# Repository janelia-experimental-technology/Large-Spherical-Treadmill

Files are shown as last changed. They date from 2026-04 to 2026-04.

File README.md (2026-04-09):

### Large Spherical Treadmill

Abstract

Recent advances in the use of the awake, head-fixed preparation for small rodents (e.g., rats and mice) have led to an array of new interactive tools for studying brain and behavior. Here we present a method for creating large, lightweight spherical treadmills of arbitrary size. To accommodate different treadmill sizes, we provide a sparse, point-based floatation mechanism that is highly scalable.

For mice (8-12 wk, 20-30 g), we present a 16” (40.64 cm, approx. 65-70 g) diameter spherical treadmill. For young-adult rats (3-8 wk, 60-150 g), we present a 24” (60.96 cm, approx. 225-275 g) diameter system.

Features \& Benefits:

&#x20;   A larger spherical diameter creates a flatter treadmill surface area that allows for a more comfortable animal and positively promotes the expression of natural behaviors (sleeping, resting, grooming, and goal-directed walking and running).

&#x20;   The point-based floatation system reduces oscillations in air-flow around the treadmill and provides excellent stability under different behavioral and recording conditions.

&#x20;   The point-based floatation and minimal frame design accommodate well for slight irregularities in, and differences between, the size of individual spherical treadmills

&#x20;   The point-based floatation system reduces air-flow and system volume

&#x20;   The minimal frame design allows for increased access to the lower half of the treadmill surface for motion-tracking and other potential manipulations

Opportunity: Free to make for Non-Profit Research by downloading the design here. See included hardware license.

Rights and designs available for Commercial License. Janelia makes no endorsements or guarantees of licensee products.

For inquiries, please contact innovation@janelia.hhmi.org and reference this repository.

To cite the designs, please use DOI: https://doi.org/10.25378/janelia.31974762

Supercedes Flintbox ID 2012-019

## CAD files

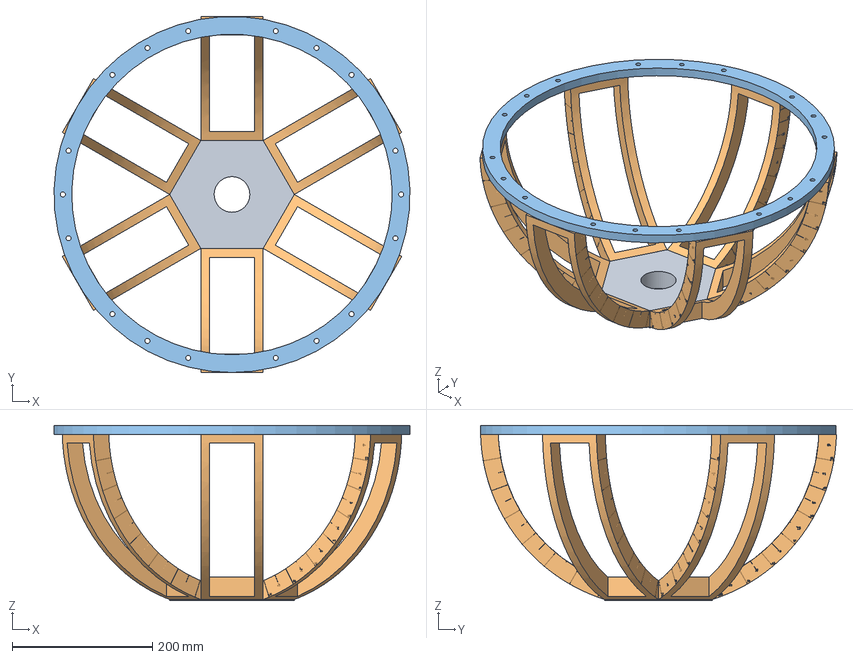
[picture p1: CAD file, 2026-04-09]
Part Drawings and Models/JF-AT-TM0006 16 inch ball treadmill assembly Rev -.stp
507.8 x 507.9 x 250.0 mm
16 inch ball treadmill frame base v2
16 inch ball treadmill frame v2 x 6
16 inch ball treadmill top ring v2

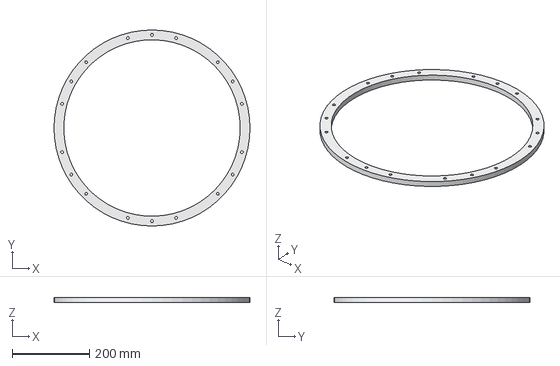
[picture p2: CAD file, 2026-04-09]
Part Drawings and Models/JF-AT-TM0008 16 inch ball treadmill top ring v2 Rev -.stp
508.0 x 508.0 x 12.7 mm

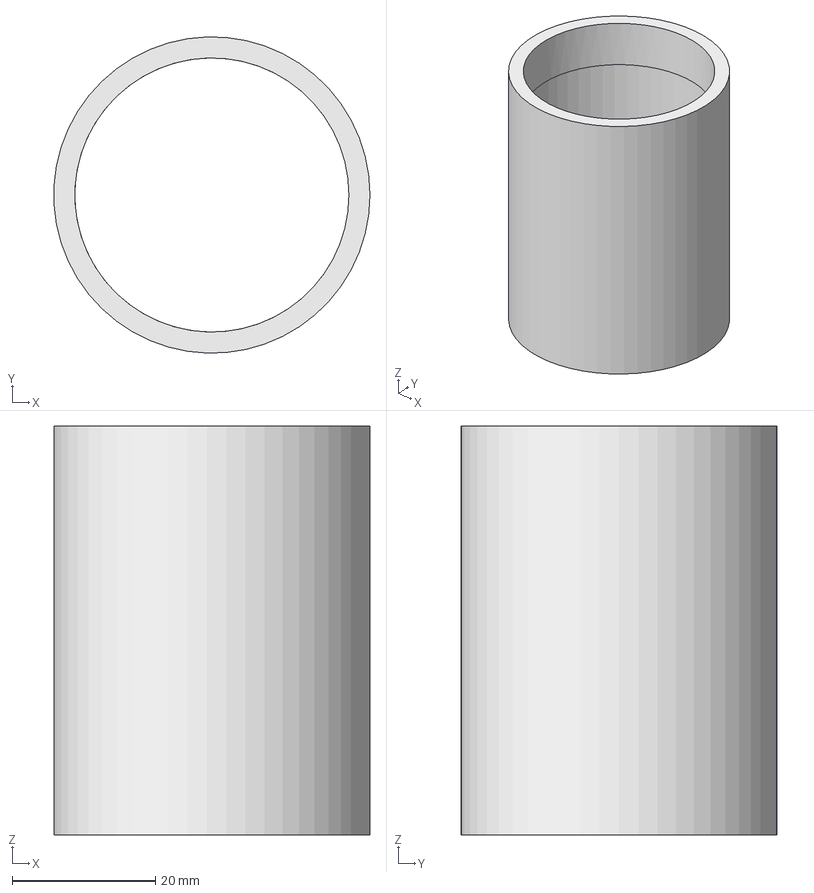
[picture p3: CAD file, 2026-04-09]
Part Drawings and Models/JF-AT-JC0005 BallHolderTubeAirBall Rev C.stp
44.2 x 44.2 x 57.1 mm

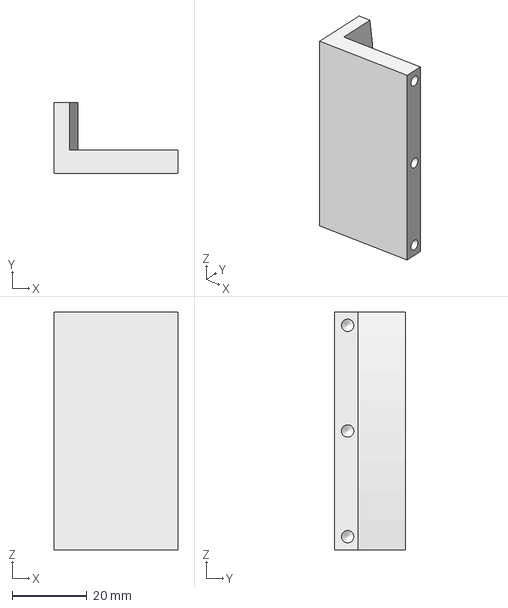
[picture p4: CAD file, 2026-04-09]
Part Drawings and Models/JF-AT-JC0016 CanClamper16 Rev A.stp
33.0 x 19.1 x 63.5 mm

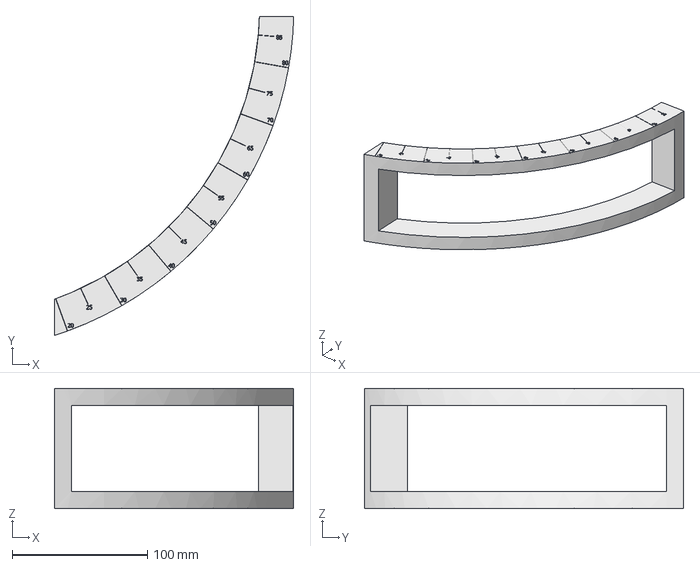
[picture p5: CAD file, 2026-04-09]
Part Drawings and Models/JF-AT-TM0007 16 inch ball treadmill frame v2 Rev -.stp
176.9 x 235.7 x 88.9 mm

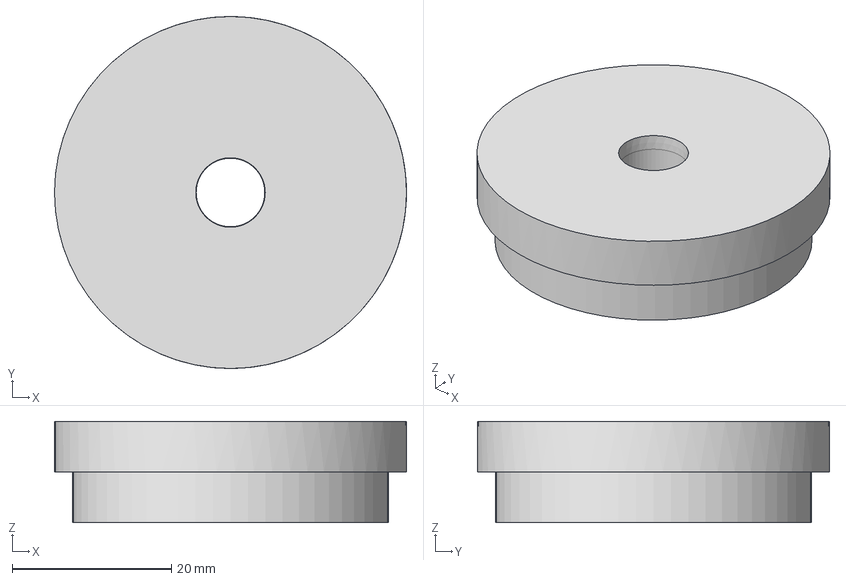
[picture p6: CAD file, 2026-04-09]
Part Drawings and Models/JF-AT-TC0007 BottomCapAirBall Rev B.stp
44.2 x 44.2 x 12.7 mm

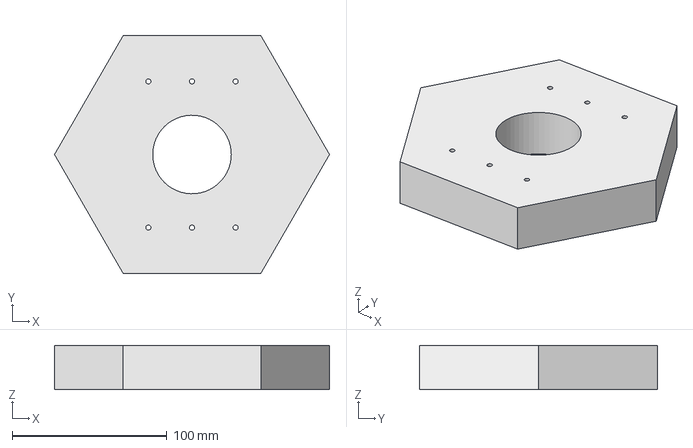
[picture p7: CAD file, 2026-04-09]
Part Drawings and Models/JF-AT-TM0009 16 inch ball treadmill frame base v2 Rev A.stp
177.8 x 154.0 x 28.4 mm

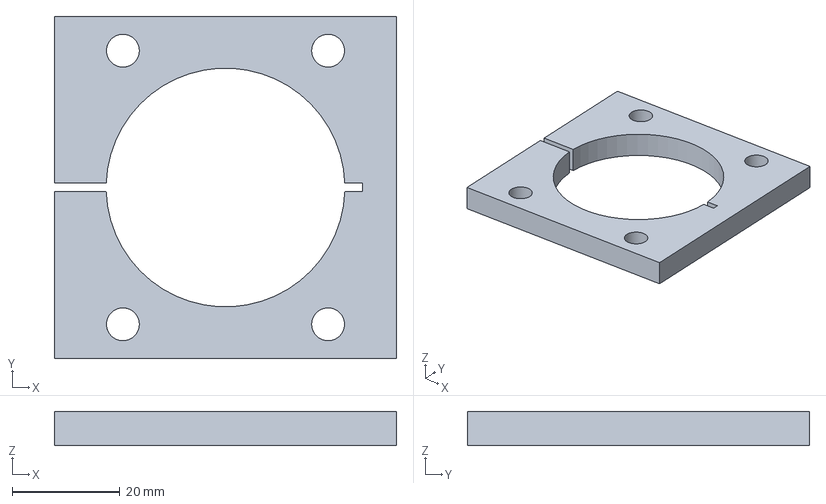
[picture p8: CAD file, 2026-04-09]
Part Drawings and Models/JF-AT-JC0015 CanClamp Rev -.stp
63.5 x 63.5 x 6.35 mm

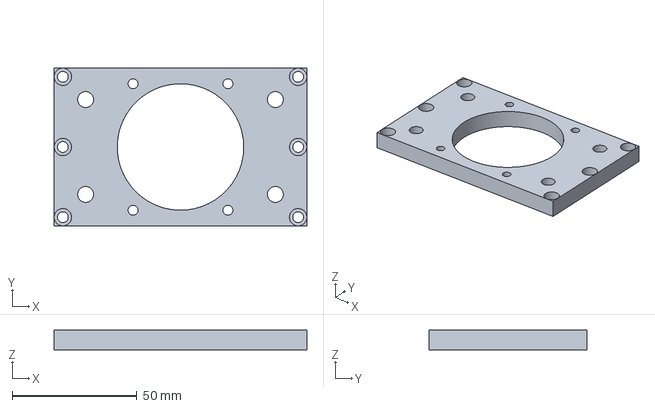
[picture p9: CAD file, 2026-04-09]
Part Drawings and Models/JF-AT-JC0014 ClamperPlate Rev -.stp
101.6 x 63.5 x 7.94 mm

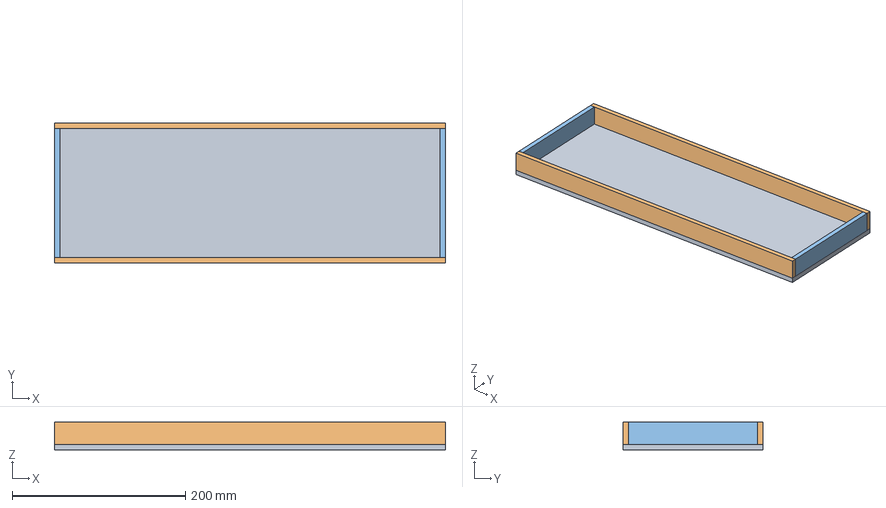
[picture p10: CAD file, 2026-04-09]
Part Drawings and Models/J005217 MBS TROUGH ASSY Rev -.stp
450.9 x 161.9 x 31.8 mm
MBS TROUGH BASE
MBS TROUGH SIDE x 2
MBS TROUGH END x 2

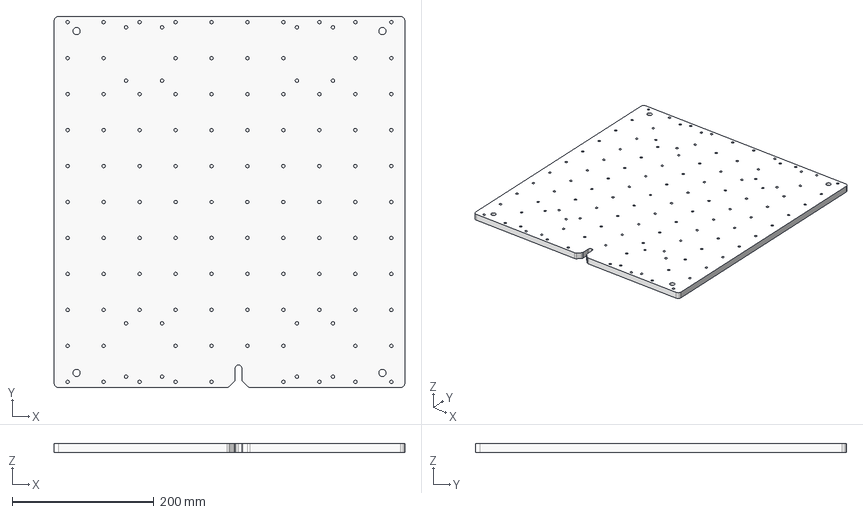
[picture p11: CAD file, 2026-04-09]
Part Drawings and Models/J003049 MBS Ball Base Plate Rev A.stp
495.3 x 523.8 x 12.7 mm

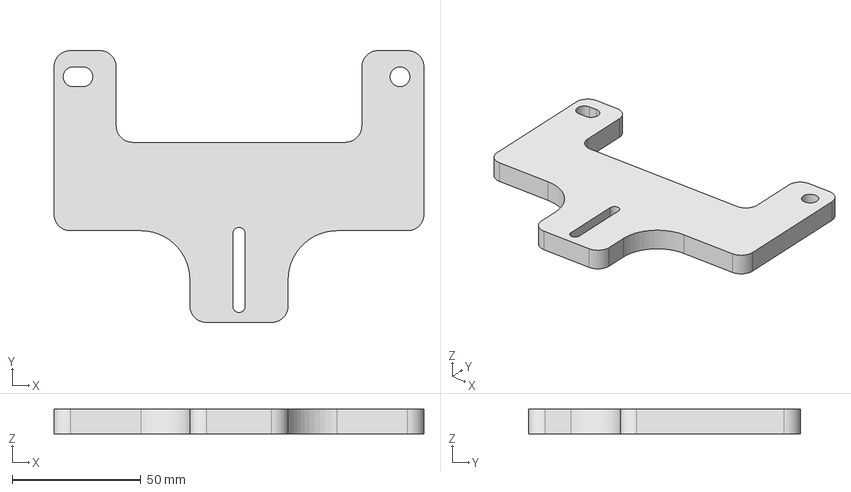
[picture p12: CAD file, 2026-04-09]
Part Drawings and Models/J005643 MBS Camera Bracket Rev -.stp
143.5 x 105.4 x 9.52 mm

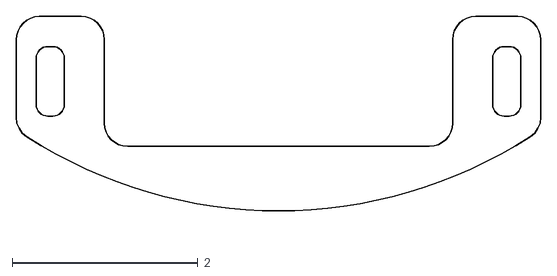
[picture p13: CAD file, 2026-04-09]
Part Drawings and Models/J005684 MBS SIDE GUIDE CONVEX Rev -.dxf
5.65 x 2.36

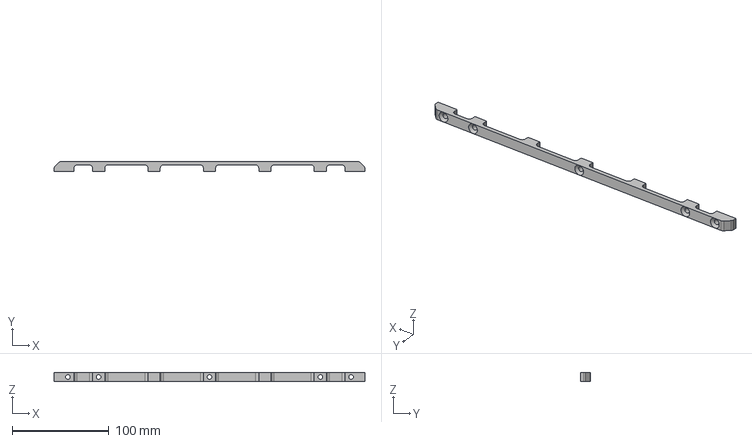
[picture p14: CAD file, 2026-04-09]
Part Drawings and Models/J005229 MBS TROUGH RAIL REV -.stp
320.7 x 10.8 x 9.52 mm

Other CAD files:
Part Drawings and Models/J005683 Ribbon Cable Connector.stp
Part Drawings and Models/J005679 Camera Front body.stp
Part Drawings and Models/J005209 MBS REG BASE PLATE REV -.stp
Part Drawings and Models/J005681 Camera Back Plate.stp
Pack and Go-Inventor Models/03-618.ipt
Pack and Go-Inventor Models/16 inch ball treadmill assembly.iam
Pack and Go-Inventor Models/16 inch ball treadmill frame base v2.ipt
Pack and Go-Inventor Models/16 inch ball treadmill frame v2.ipt
Pack and Go-Inventor Models/16 inch ball treadmill top ring v2.ipt
Pack and Go-Inventor Models/321527B00000G.ipt
Pack and Go-Inventor Models/50745K150.ipt
Pack and Go-Inventor Models/50785K213.ipt
Pack and Go-Inventor Models/50785K410.ipt
Pack and Go-Inventor Models/5779K109.ipt
Pack and Go-Inventor Models/5779K143.ipt
Pack and Go-Inventor Models/6516T13.ipt
Pack and Go-Inventor Models/90107A010.ipt
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

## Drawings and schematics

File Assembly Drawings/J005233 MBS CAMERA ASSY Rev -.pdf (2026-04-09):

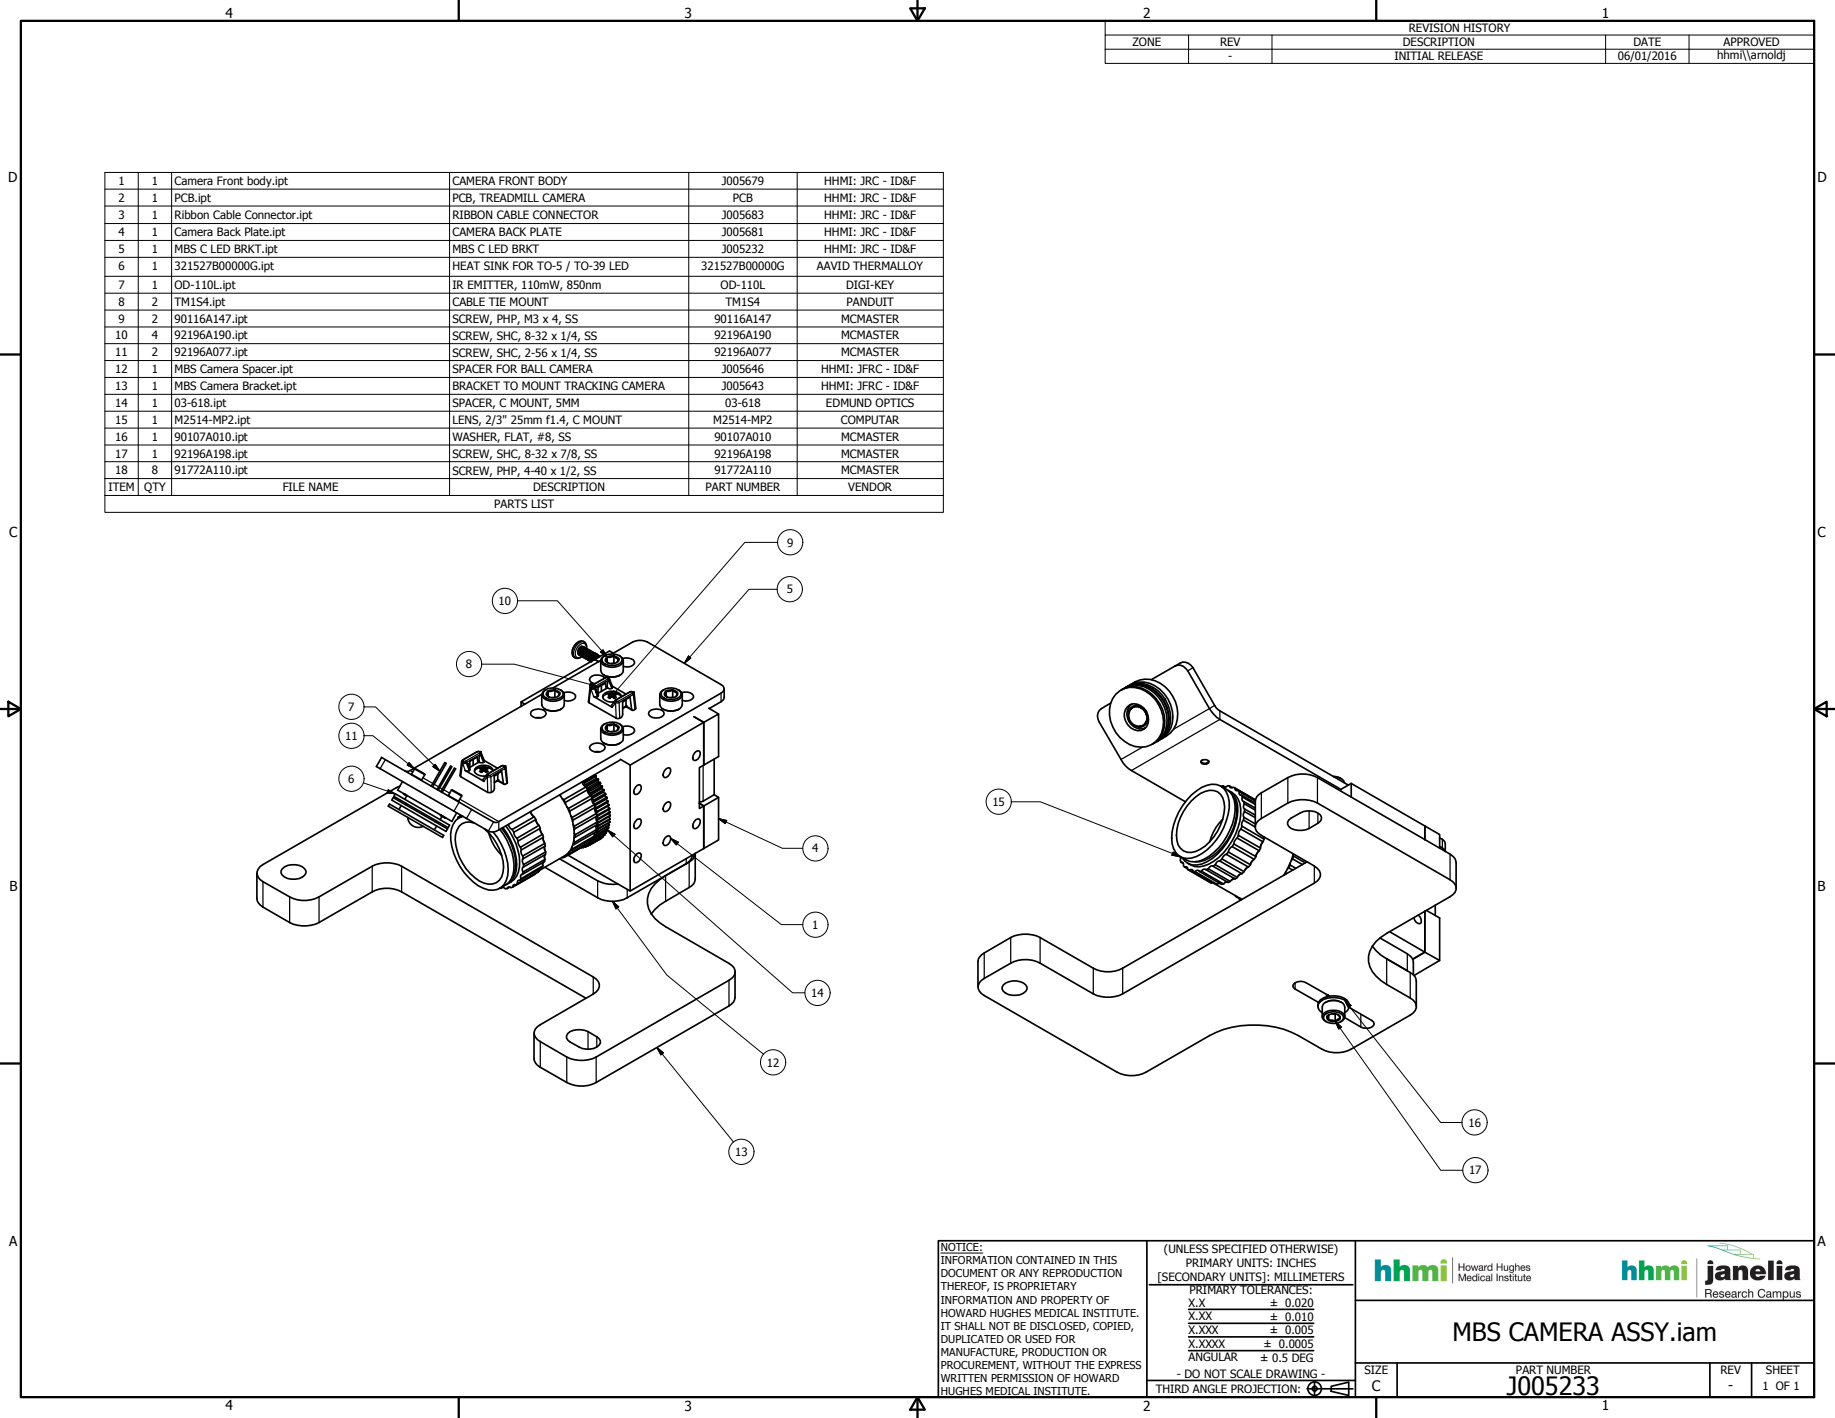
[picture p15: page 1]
Camera Front body.ipt; CAMERA FRONT BODY; HHMI: JRC - ID&F; PCB.ipt; PCB, TREADMILL CAMERA; PCB; Ribbon Cable Connector.ipt; RIBBON CABLE CONNECTOR; Camera Back Plate.ipt; CAMERA BACK PLATE; MBS C LED BRKT.ipt; MBS C LED BRKT; 321527B00000G.ipt; HEAT SINK FOR TO-5 / TO-39 LED; AAVID THERMALLOY; OD-110L.ipt; IR EMITTER, 110mW, 850nm; DIGI-KEY; TM1S4.ipt; CABLE TIE MOUNT; PANDUIT; 90116A147.ipt; SCREW, PHP, M3 x 4, SS; MCMASTER; 92196A190.ipt; SCREW, SHC, 8-32 x 1/4, SS; 92196A077.ipt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

NOTICE:
INFORMATION CONTAINED IN THIS
DOCUMENT OR ANY REPRODUCTION
THEREOF, IS PROPRIETARY
INFORMATION AND PROPERTY OF
HOWARD HUGHES MEDICAL INSTITUTE.
IT SHALL NOT BE DISCLOSED, COPIED,
DUPLICATED OR USED FOR
MANUFACTURE, PRODUCTION OR
PROCUREMENT, WITHOUT THE EXPRESS
WRITTEN PERMISSION OF HOWARD
HUGHES MEDICAL INSTITUTE.

(UNLESS SPECIFIED OTHERWISE)
PRIMARY UNITS: INCHES
[SECONDARY UNITS]: MILLIMETERS
PRIMARY TOLERANCES:
X.XXX
X.XXXX
ANGULAR
- DO NOT SCALE DRAWING -

MBS CAMERA ASSY.iam

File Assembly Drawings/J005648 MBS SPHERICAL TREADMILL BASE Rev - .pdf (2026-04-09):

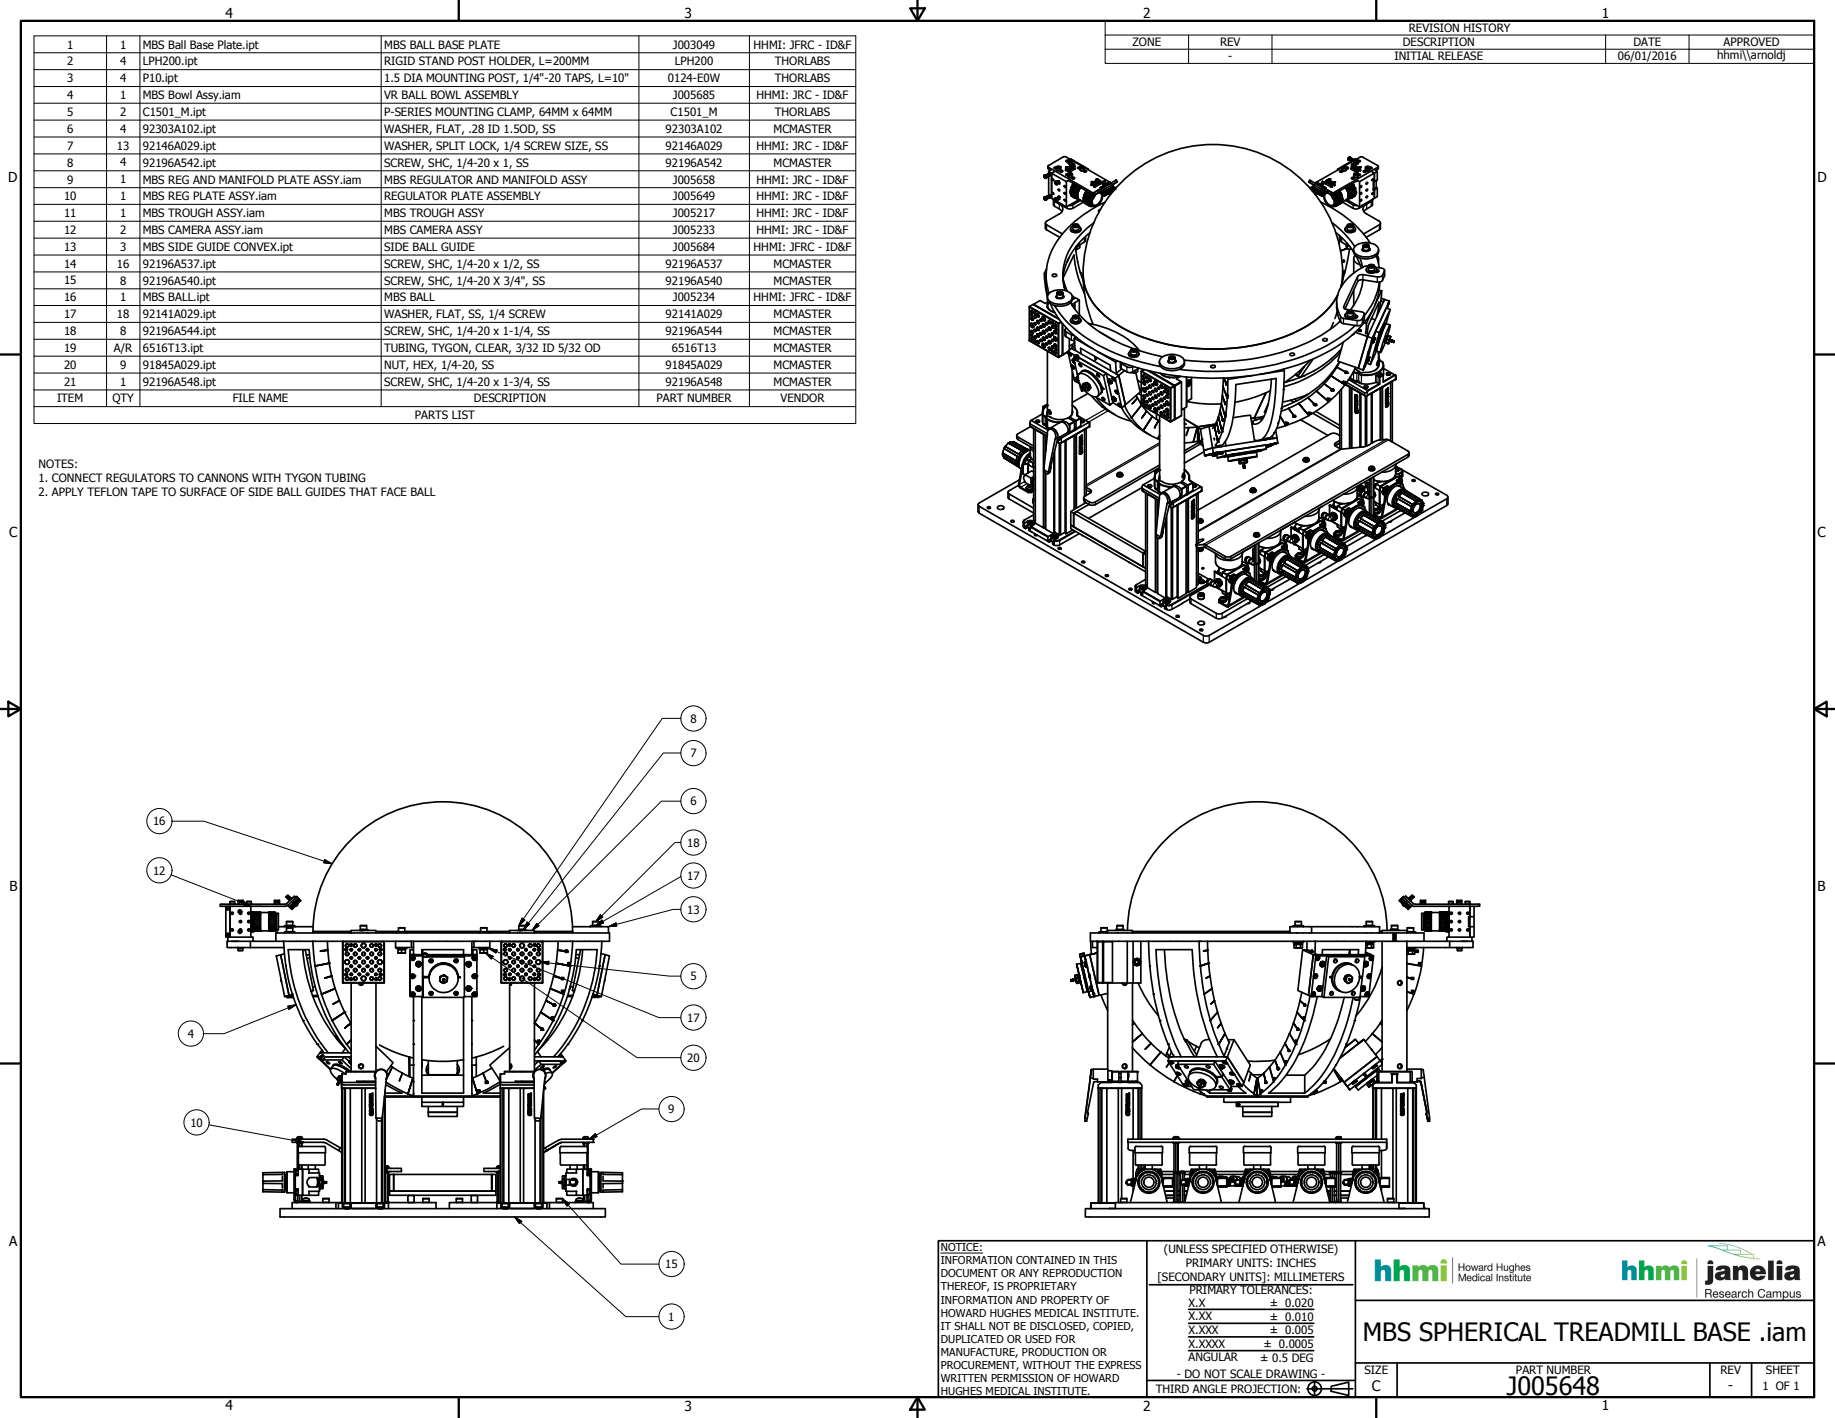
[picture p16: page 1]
MBS Ball Base Plate.ipt; MBS BALL BASE PLATE; HHMI: JFRC - ID&F; LPH200.ipt; RIGID STAND POST HOLDER, L=200MM; LPH200; THORLABS; P10.ipt; 1.5 DIA MOUNTING POST, 1/4"-20 TAPS, L=10"; MBS Bowl Assy.iam; VR BALL BOWL ASSEMBLY; HHMI: JRC - ID&F; C1501_M.ipt; P-SERIES MOUNTING CLAMP, 64MM x 64MM; 92303A102.ipt; WASHER, FLAT, .28 ID 1.5OD, SS; MCMASTER; 13 92146A029.ipt; WASHER, SPLIT LOCK, 1/4 SCREW SIZE, SS; 92196A542.ipt; SCREW, SHC, 1/4-20 x 1, SS; MBS REG AND MANIFOLD PLATE ASSY.iam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

NOTES:
1. CONNECT REGULATORS TO CANNONS WITH TYGON TUBING
2. APPLY TEFLON TAPE TO SURFACE OF SIDE BALL GUIDES THAT FACE BALL

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

MBS SPHERICAL TREADMILL BASE .iam

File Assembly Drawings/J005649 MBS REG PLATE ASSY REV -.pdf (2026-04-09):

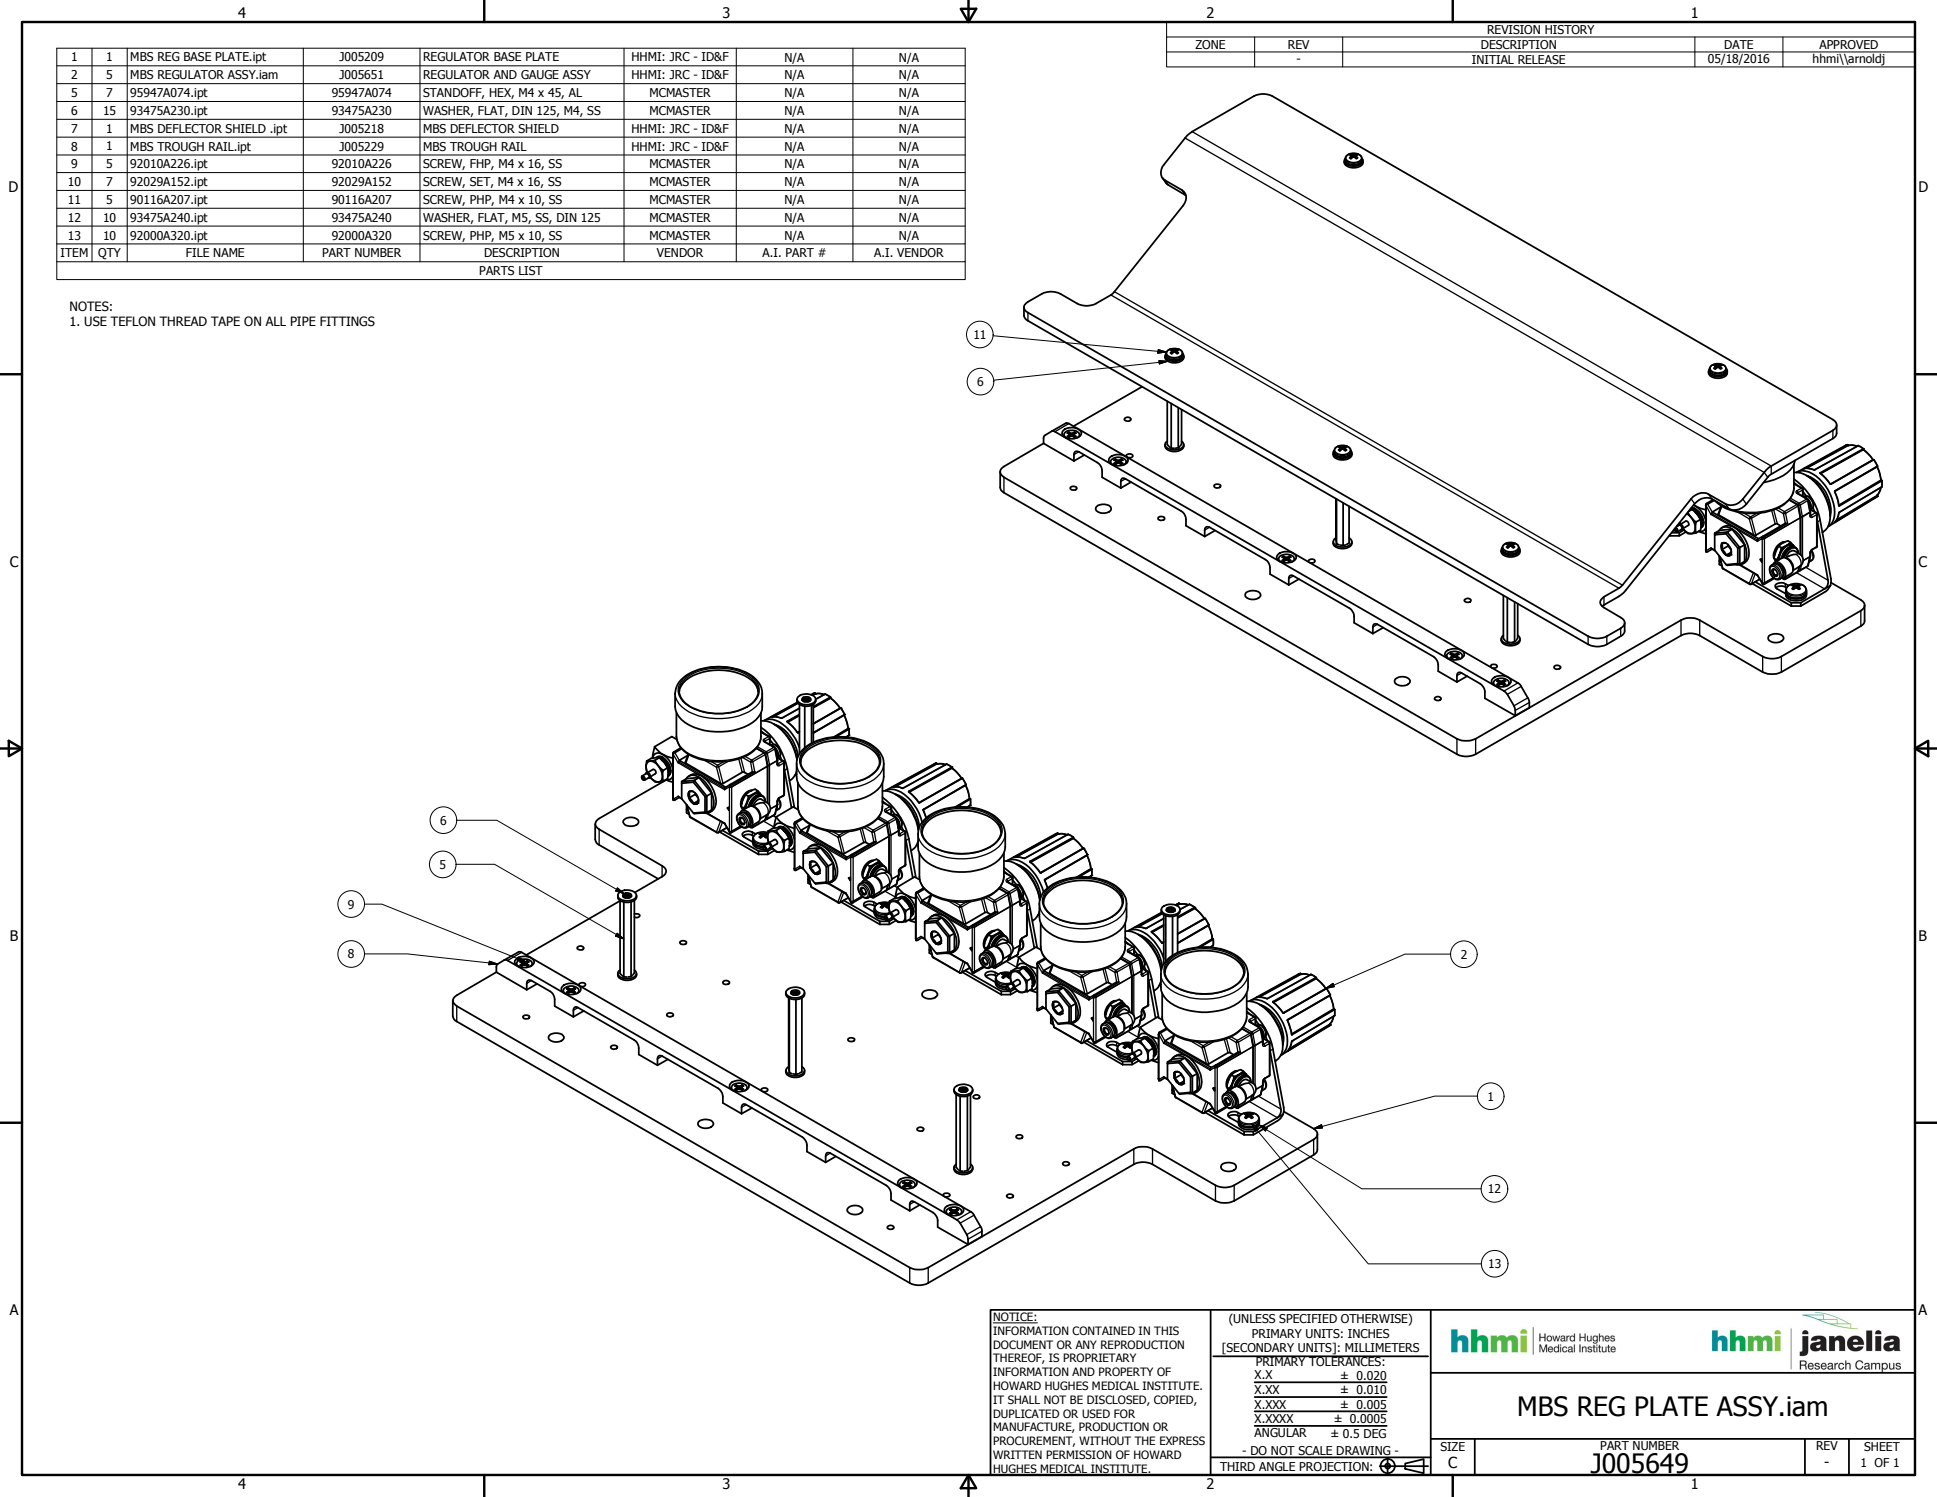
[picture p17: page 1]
92000A320.ipt; SCREW, PHP, M5 x 10, SS; MCMASTER; PARTS LIST; ITEM; QTY; FILE NAME; PART NUMBER; DESCRIPTION; VENDOR; A.I. PART #; A.I. VENDOR; SIZE; REV; SHEET; 1 OF 1 THIRD ANGLE PROJECTION:; ± 0.020 ± 0.010 ± 0.005 ± 0.0005 ± 0.5 DEG; REVISION HISTORY; ZONE; DATE; APPROVED; INITIAL RELEASE; hhmi\\arnoldj

1 | 1 | MBS REG BASE PLATE.ipt | J005209 | REGULATOR BASE PLATE | HHMI: JRC - ID&F | N/A | N/A
2 | 5 | MBS REGULATOR ASSY.iam | J005651 | REGULATOR AND GAUGE ASSY | HHMI: JRC - ID&F | N/A | N/A
5 | 7 | 95947A074.ipt | 95947A074 | STANDOFF, HEX, M4 x 45, AL | MCMASTER | N/A | N/A
6 | 15 | 93475A230.ipt | 93475A230 | WASHER, FLAT, DIN 125, M4, SS | MCMASTER | N/A | N/A
7 | 1 | MBS DEFLECTOR SHIELD .ipt | J005218 | MBS DEFLECTOR SHIELD | HHMI: JRC - ID&F | N/A | N/A
8 | 1 | MBS TROUGH RAIL.ipt | J005229 | MBS TROUGH RAIL | HHMI: JRC - ID&F | N/A | N/A
9 | 5 | 92010A226.ipt | 92010A226 | SCREW, FHP, M4 x 16, SS | MCMASTER | N/A | N/A
10 | 7 | 92029A152.ipt | 92029A152 | SCREW, SET, M4 x 16, SS | MCMASTER | N/A | N/A
11 | 5 | 90116A207.ipt | 90116A207 | SCREW, PHP, M4 x 10, SS | MCMASTER | N/A | N/A
12 | 10 | 93475A240.ipt | 93475A240 | WASHER, FLAT, M5, SS, DIN 125 | MCMASTER | N/A | N/A

NOTES:
1. USE TEFLON THREAD TAPE ON ALL PIPE FITTINGS

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

MBS REG PLATE ASSY.iam

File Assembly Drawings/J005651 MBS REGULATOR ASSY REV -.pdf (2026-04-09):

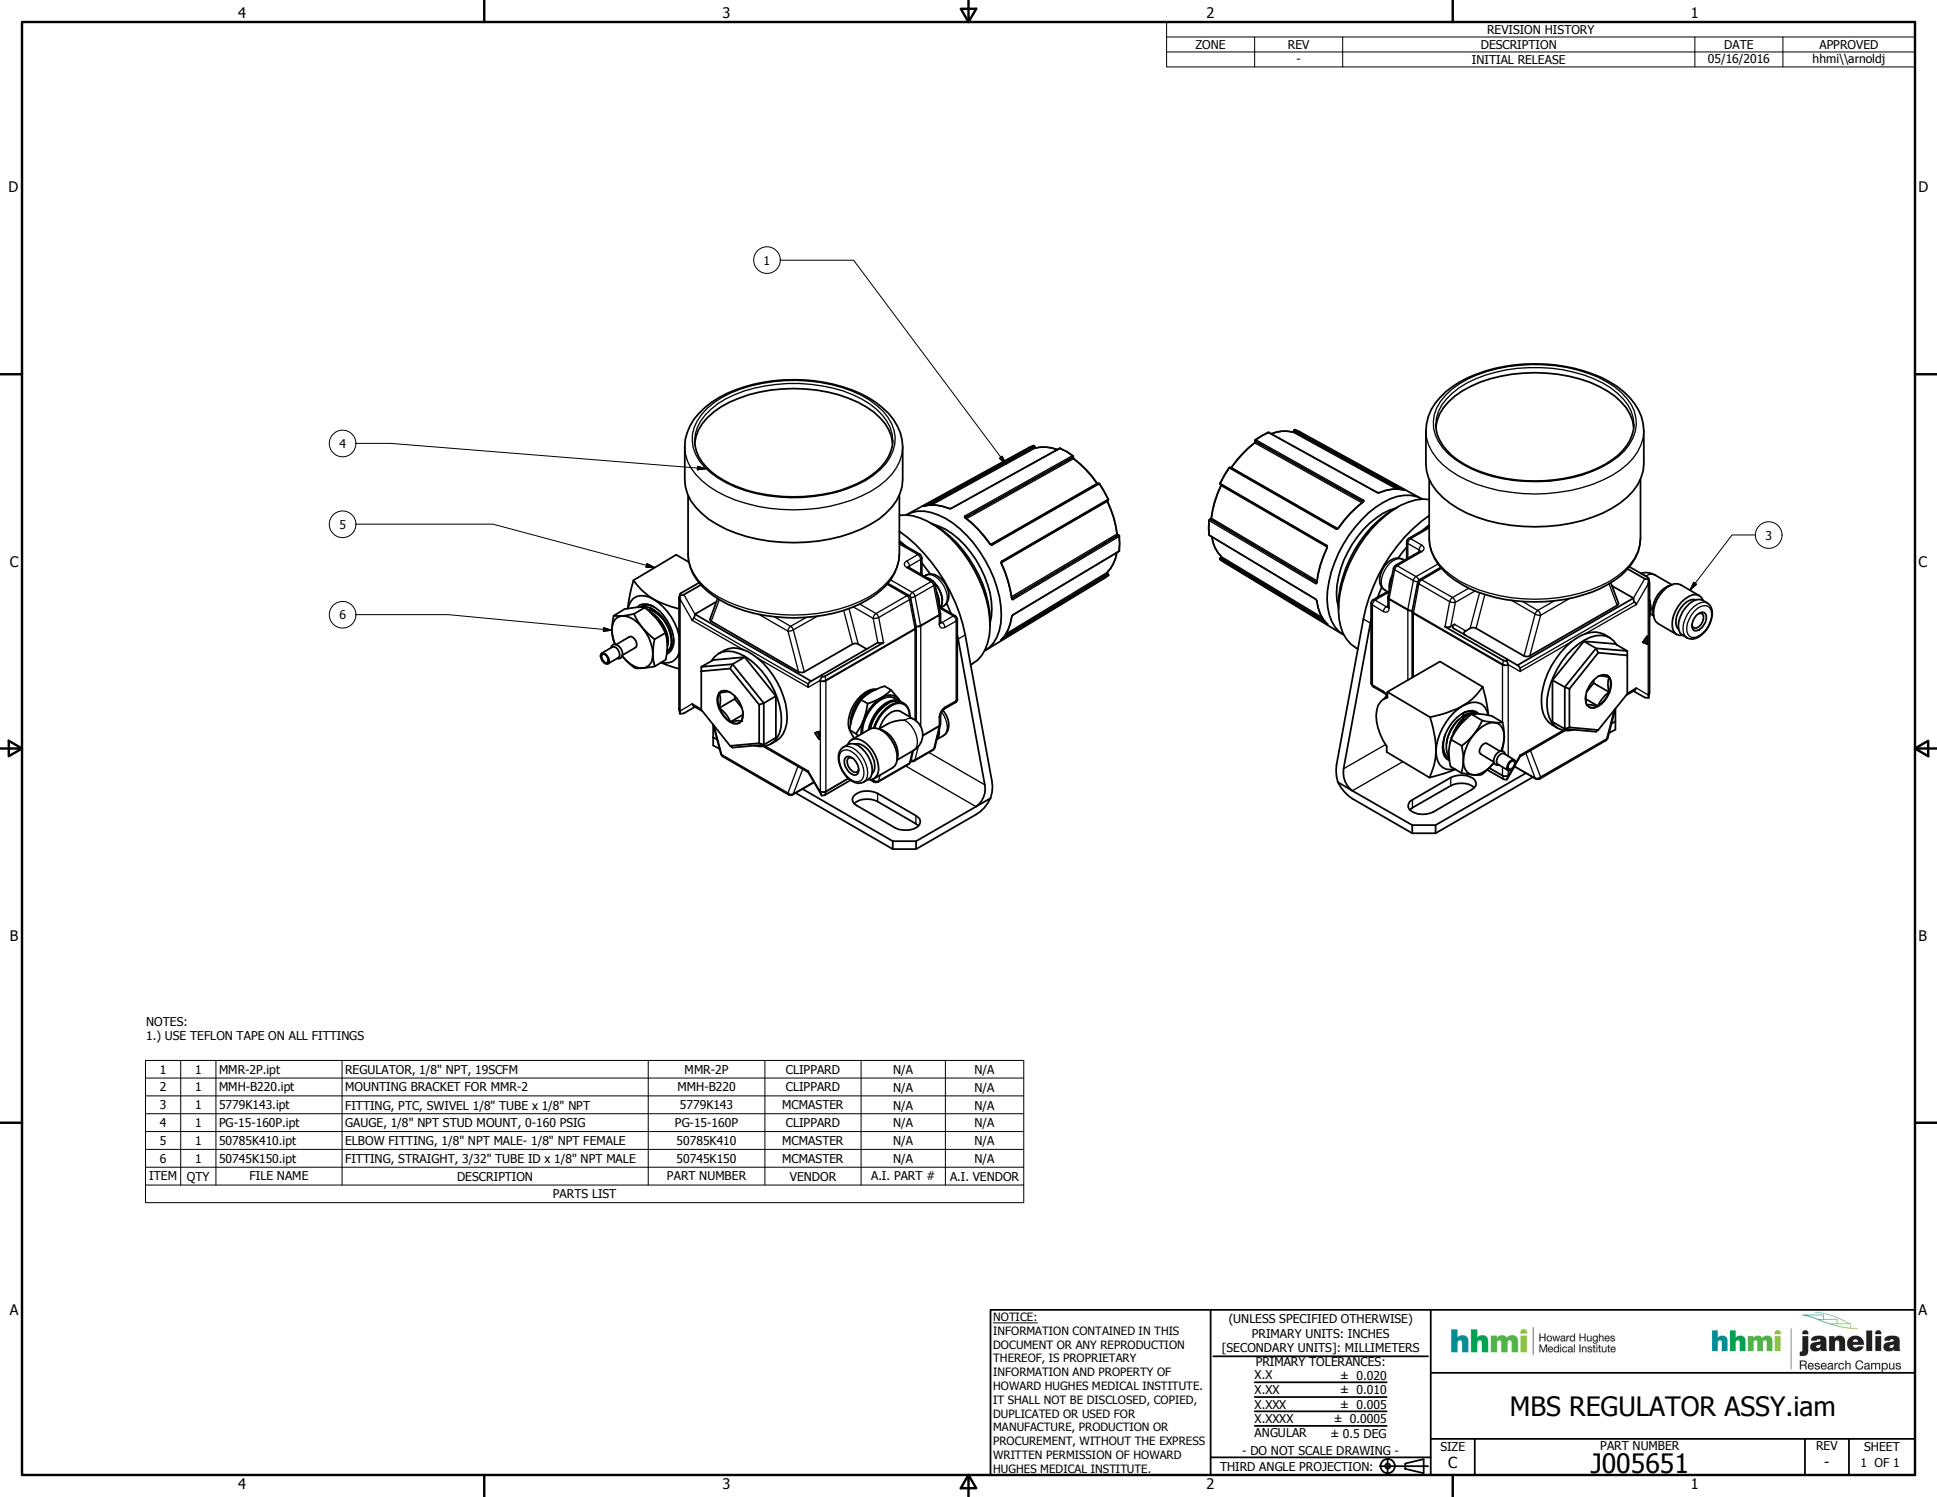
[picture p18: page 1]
MMR-2P.ipt; REGULATOR, 1/8" NPT, 19SCFM; MMR-2P; CLIPPARD; MMH-B220.ipt; MOUNTING BRACKET FOR MMR-2; MMH-B220; 5779K143.ipt; FITTING, PTC, SWIVEL 1/8" TUBE x 1/8" NPT; MCMASTER; PG-15-160P.ipt; GAUGE, 1/8" NPT STUD MOUNT, 0-160 PSIG; 50785K410.ipt; ELBOW FITTING, 1/8" NPT MALE- 1/8" NPT FEMALE; 50745K150.ipt; FITTING, STRAIGHT, 3/32" TUBE ID x 1/8" NPT MALE; PARTS LIST; ITEM; QTY; FILE NAME; DESCRIPTION; PART NUMBER; VENDOR; A.I. PART #; A.I. VENDOR; SIZE; REV; SHEET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

NOTES:
1.) USE TEFLON TAPE ON ALL FITTINGS

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

MBS REGULATOR ASSY.iam

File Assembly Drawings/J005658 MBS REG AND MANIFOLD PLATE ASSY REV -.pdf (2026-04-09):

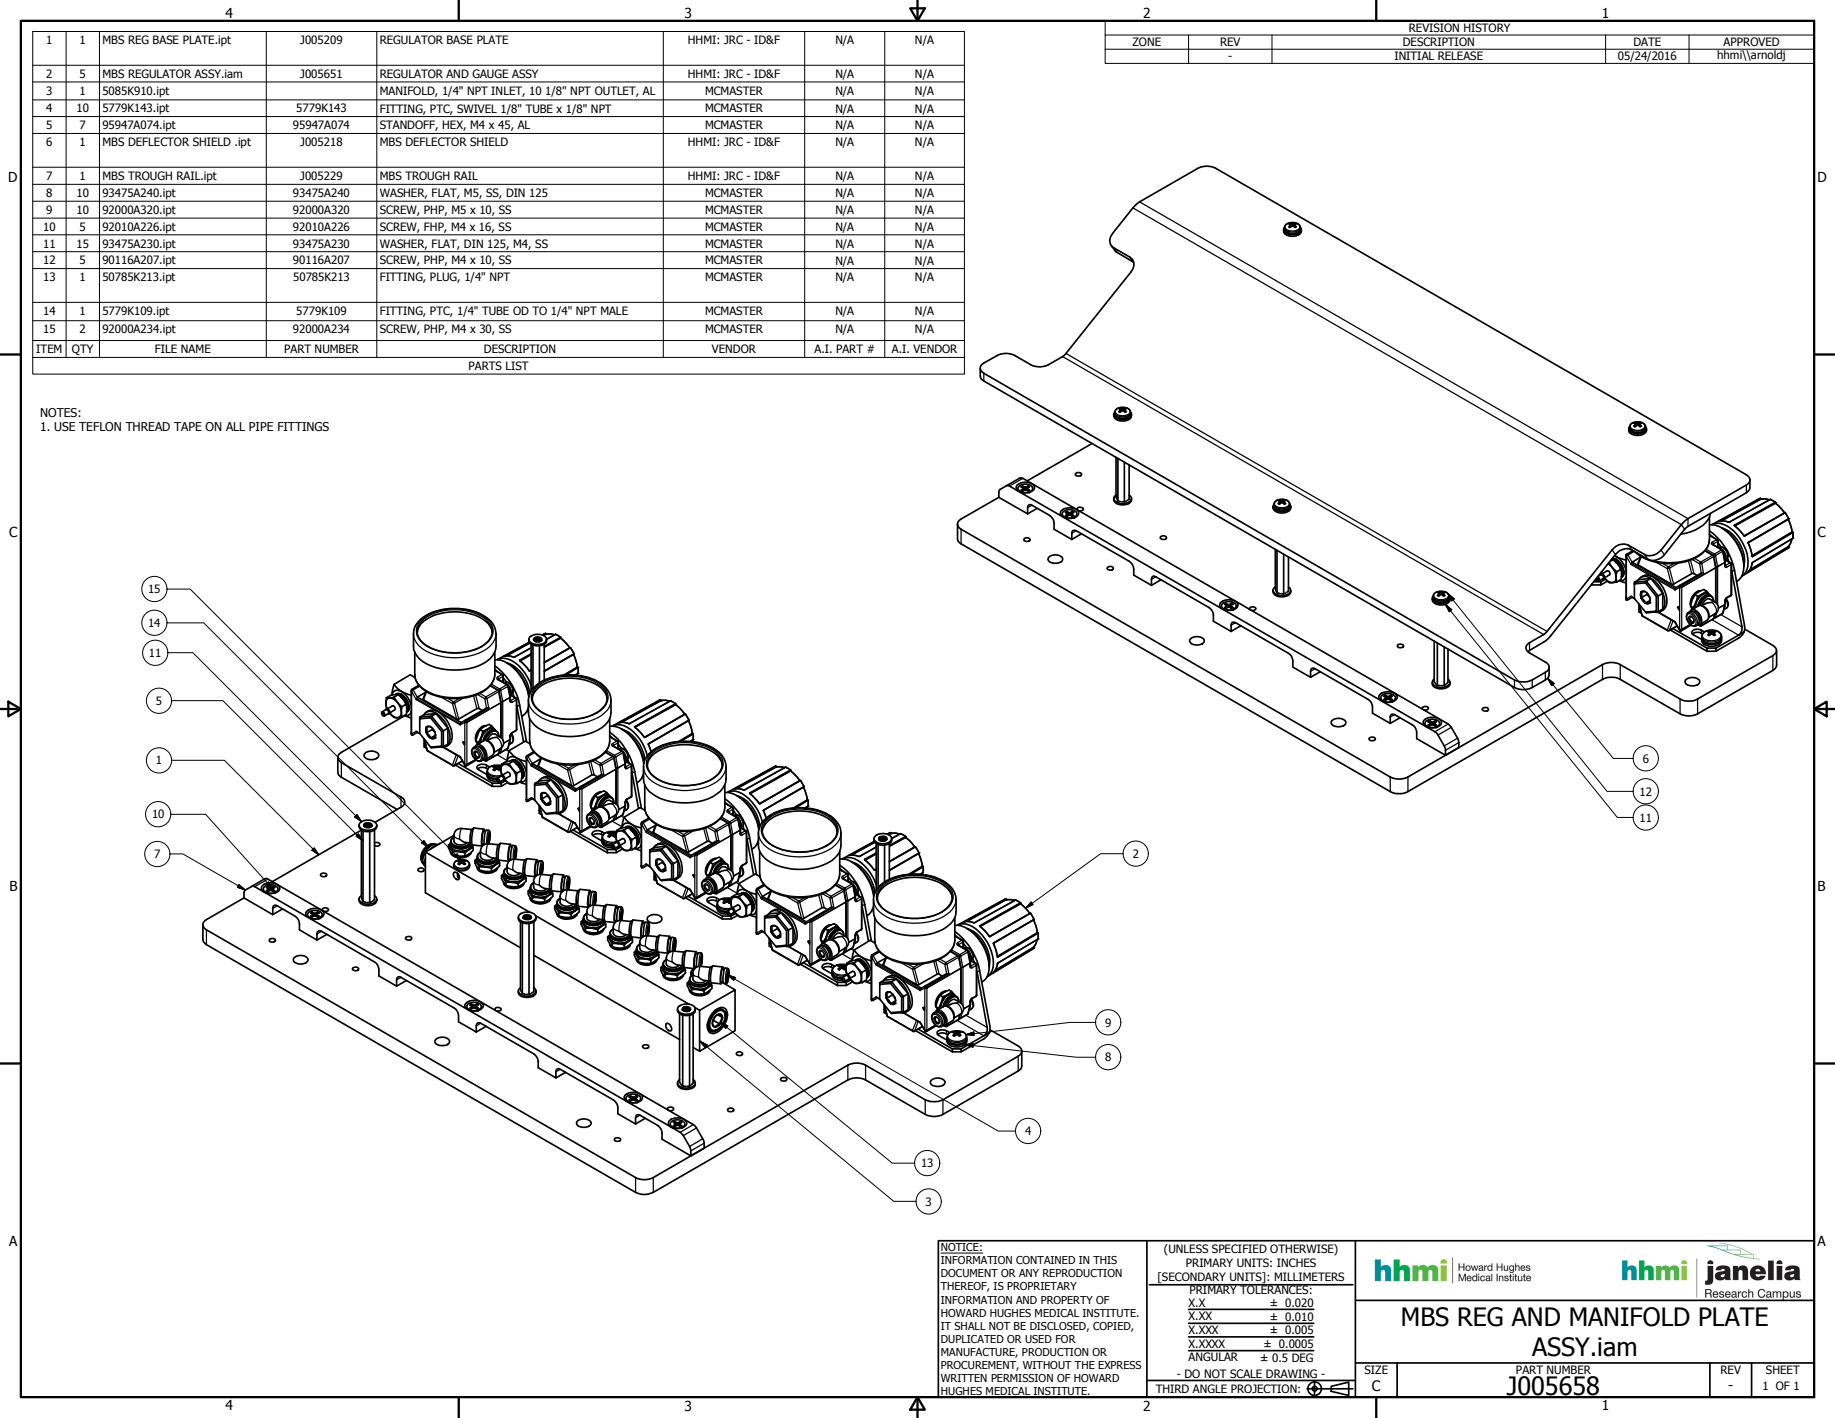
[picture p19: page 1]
MBS REG BASE PLATE.ipt; REGULATOR BASE PLATE; HHMI: JRC - ID&F; 92000A234.ipt; SCREW, PHP, M4 x 30, SS; MCMASTER; PARTS LIST; ITEM; QTY; FILE NAME; PART NUMBER; DESCRIPTION; VENDOR; A.I. PART #; A.I. VENDOR; SIZE; REV; SHEET; 1 OF 1 THIRD ANGLE PROJECTION:; ± 0.020 ± 0.010 ± 0.005 ± 0.0005 ± 0.5 DEG; ASSY.iam; REVISION HISTORY; ZONE; DATE; APPROVED; INITIAL RELEASE; hhmi\\arnoldj

2 | 5 | MBS REGULATOR ASSY.iam | J005651 | REGULATOR AND GAUGE ASSY | HHMI: JRC - ID&F | N/A | N/A
3 | 1 | 5085K910.ipt | | MANIFOLD, 1/4" NPT INLET, 10 1/8" NPT OUTLET, AL | MCMASTER | N/A | N/A
4 | 10 | 5779K143.ipt | 5779K143 | FITTING, PTC, SWIVEL 1/8" TUBE x 1/8" NPT | MCMASTER | N/A | N/A
5 | 7 | 95947A074.ipt | 95947A074 | STANDOFF, HEX, M4 x 45, AL | MCMASTER | N/A | N/A
6 | 1 | MBS DEFLECTOR SHIELD .ipt | J005218 | MBS DEFLECTOR SHIELD | HHMI: JRC - ID&F | N/A | N/A

7 | 1 | MBS TROUGH RAIL.ipt | J005229 | MBS TROUGH RAIL | HHMI: JRC - ID&F | N/A | N/A
8 | 10 | 93475A240.ipt | 93475A240 | WASHER, FLAT, M5, SS, DIN 125 | MCMASTER | N/A | N/A
9 | 10 | 92000A320.ipt | 92000A320 | SCREW, PHP, M5 x 10, SS | MCMASTER | N/A | N/A
10 | 5 | 92010A226.ipt | 92010A226 | SCREW, FHP, M4 x 16, SS | MCMASTER | N/A | N/A
11 | 15 | 93475A230.ipt | 93475A230 | WASHER, FLAT, DIN 125, M4, SS | MCMASTER | N/A | N/A
12 | 5 | 90116A207.ipt | 90116A207 | SCREW, PHP, M4 x 10, SS | MCMASTER | N/A | N/A
13 | 1 | 50785K213.ipt | 50785K213 | FITTING, PLUG, 1/4" NPT | MCMASTER | N/A | N/A

14 | 1 | 5779K109.ipt | 5779K109 | FITTING, PTC, 1/4" TUBE OD TO 1/4" NPT MALE | MCMASTER | N/A | N/A

NOTES:
1. USE TEFLON THREAD TAPE ON ALL PIPE FITTINGS

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

MBS REG AND MANIFOLD PLATE

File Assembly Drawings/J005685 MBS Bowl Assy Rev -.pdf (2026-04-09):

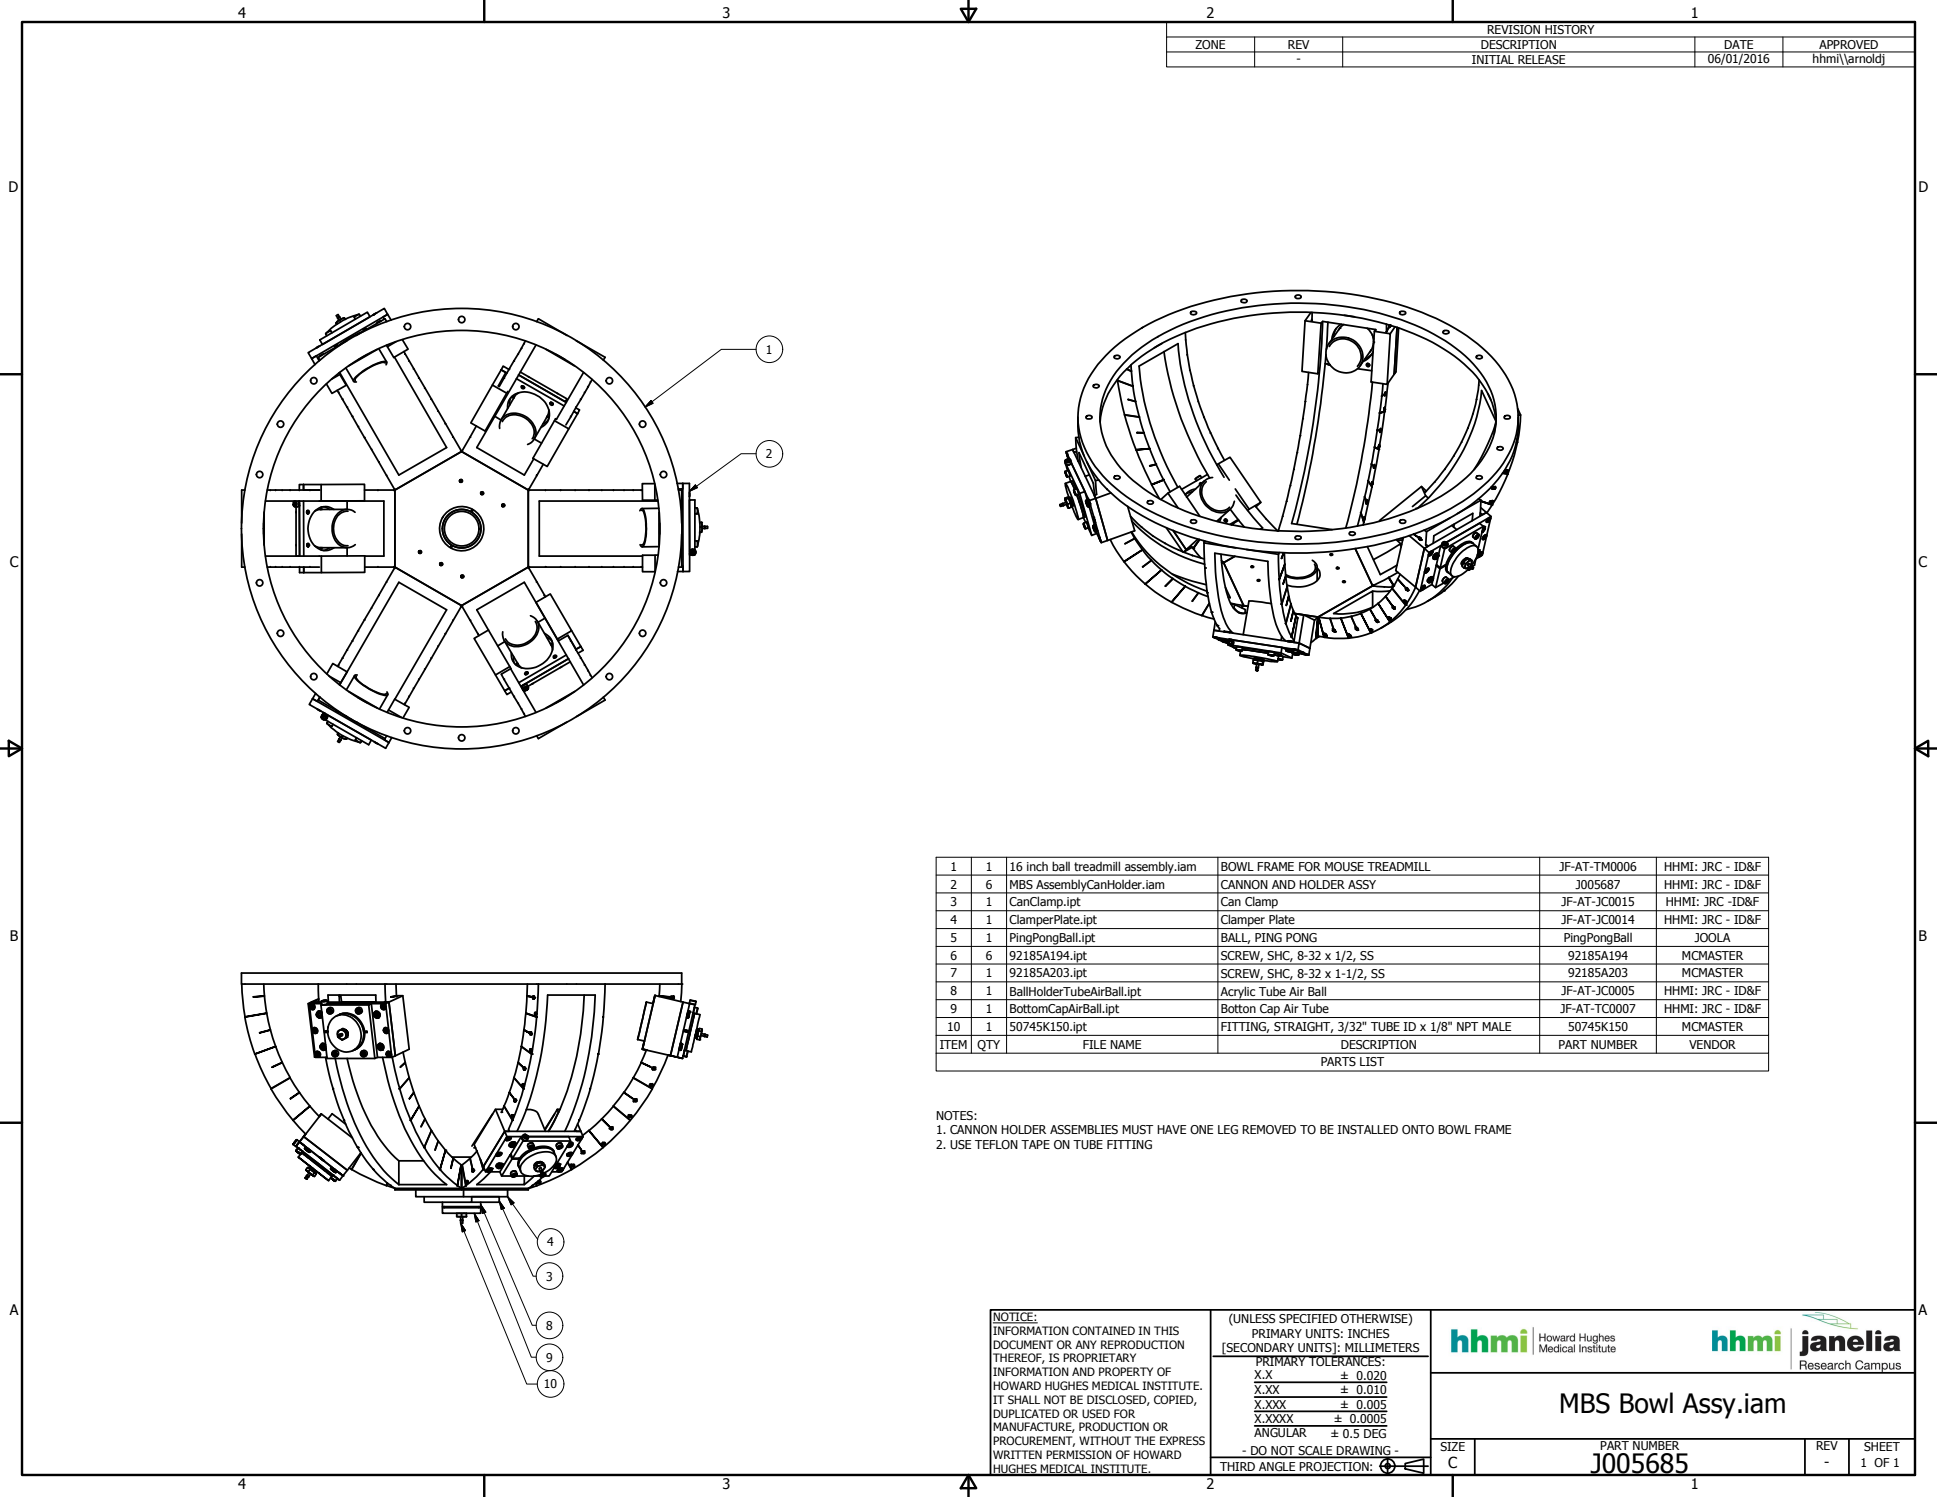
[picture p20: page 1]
16 inch ball treadmill assembly.iam; BOWL FRAME FOR MOUSE TREADMILL; HHMI: JRC - ID&F; MBS AssemblyCanHolder.iam; CANNON AND HOLDER ASSY; CanClamp.ipt; Can Clamp; HHMI: JRC -ID&F; ClamperPlate.ipt; Clamper Plate; PingPongBall.ipt; BALL, PING PONG; PingPongBall; JOOLA; 92185A194.ipt; SCREW, SHC, 8-32 x 1/2, SS; MCMASTER; 92185A203.ipt; SCREW, SHC, 8-32 x 1-1/2, SS; BallHolderTubeAirBall.ipt; Acrylic Tube Air Ball; BottomCapAirBall.ipt; Botton Cap Air Tube; 50745K150.ipt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

NOTES:
1. CANNON HOLDER ASSEMBLIES MUST HAVE ONE LEG REMOVED TO BE INSTALLED ONTO BOWL FRAME
2. USE TEFLON TAPE ON TUBE FITTING

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

MBS Bowl Assy.iam

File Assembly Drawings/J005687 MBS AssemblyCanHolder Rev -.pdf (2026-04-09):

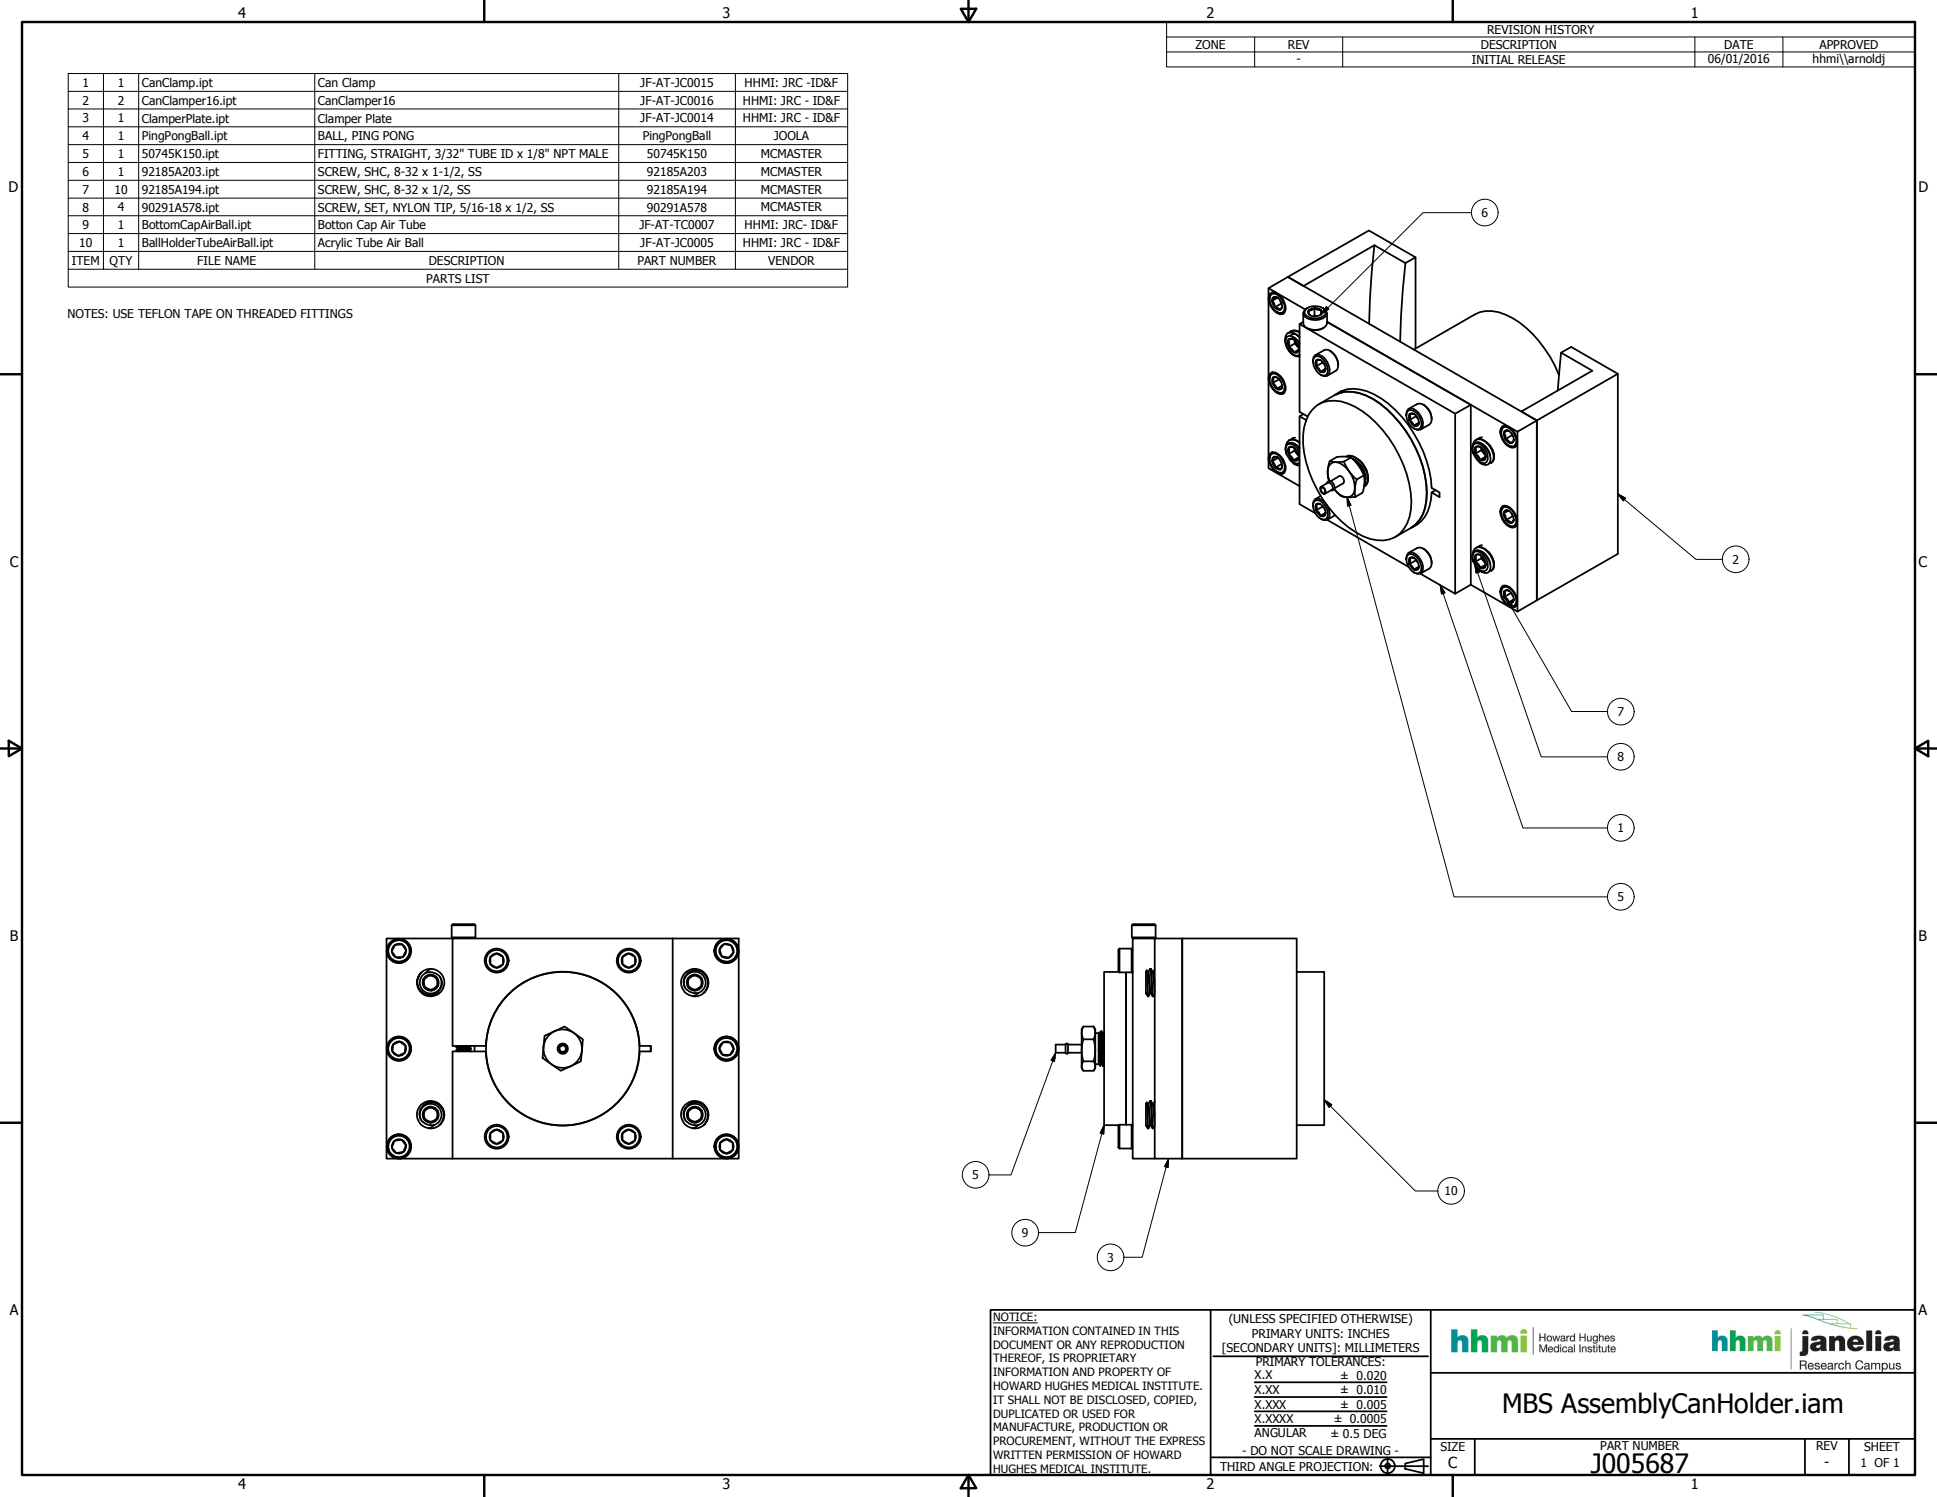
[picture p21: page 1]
CanClamp.ipt; Can Clamp; HHMI: JRC -ID&F; CanClamper16.ipt; CanClamper16; HHMI: JRC - ID&F; ClamperPlate.ipt; Clamper Plate; PingPongBall.ipt; BALL, PING PONG; PingPongBall; JOOLA; 50745K150.ipt; FITTING, STRAIGHT, 3/32" TUBE ID x 1/8" NPT MALE; MCMASTER; 92185A203.ipt; SCREW, SHC, 8-32 x 1-1/2, SS; 92185A194.ipt; SCREW, SHC, 8-32 x 1/2, SS; 90291A578.ipt; SCREW, SET, NYLON TIP, 5/16-18 x 1/2, SS; BottomCapAirBall.ipt; Botton Cap Air Tube; HHMI: JRC- ID&F; BallHolderTubeAirBall.ipt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

NOTES: USE TEFLON TAPE ON THREADED FITTINGS

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

MBS AssemblyCanHolder.iam

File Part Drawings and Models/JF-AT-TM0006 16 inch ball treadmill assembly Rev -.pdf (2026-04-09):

1

2

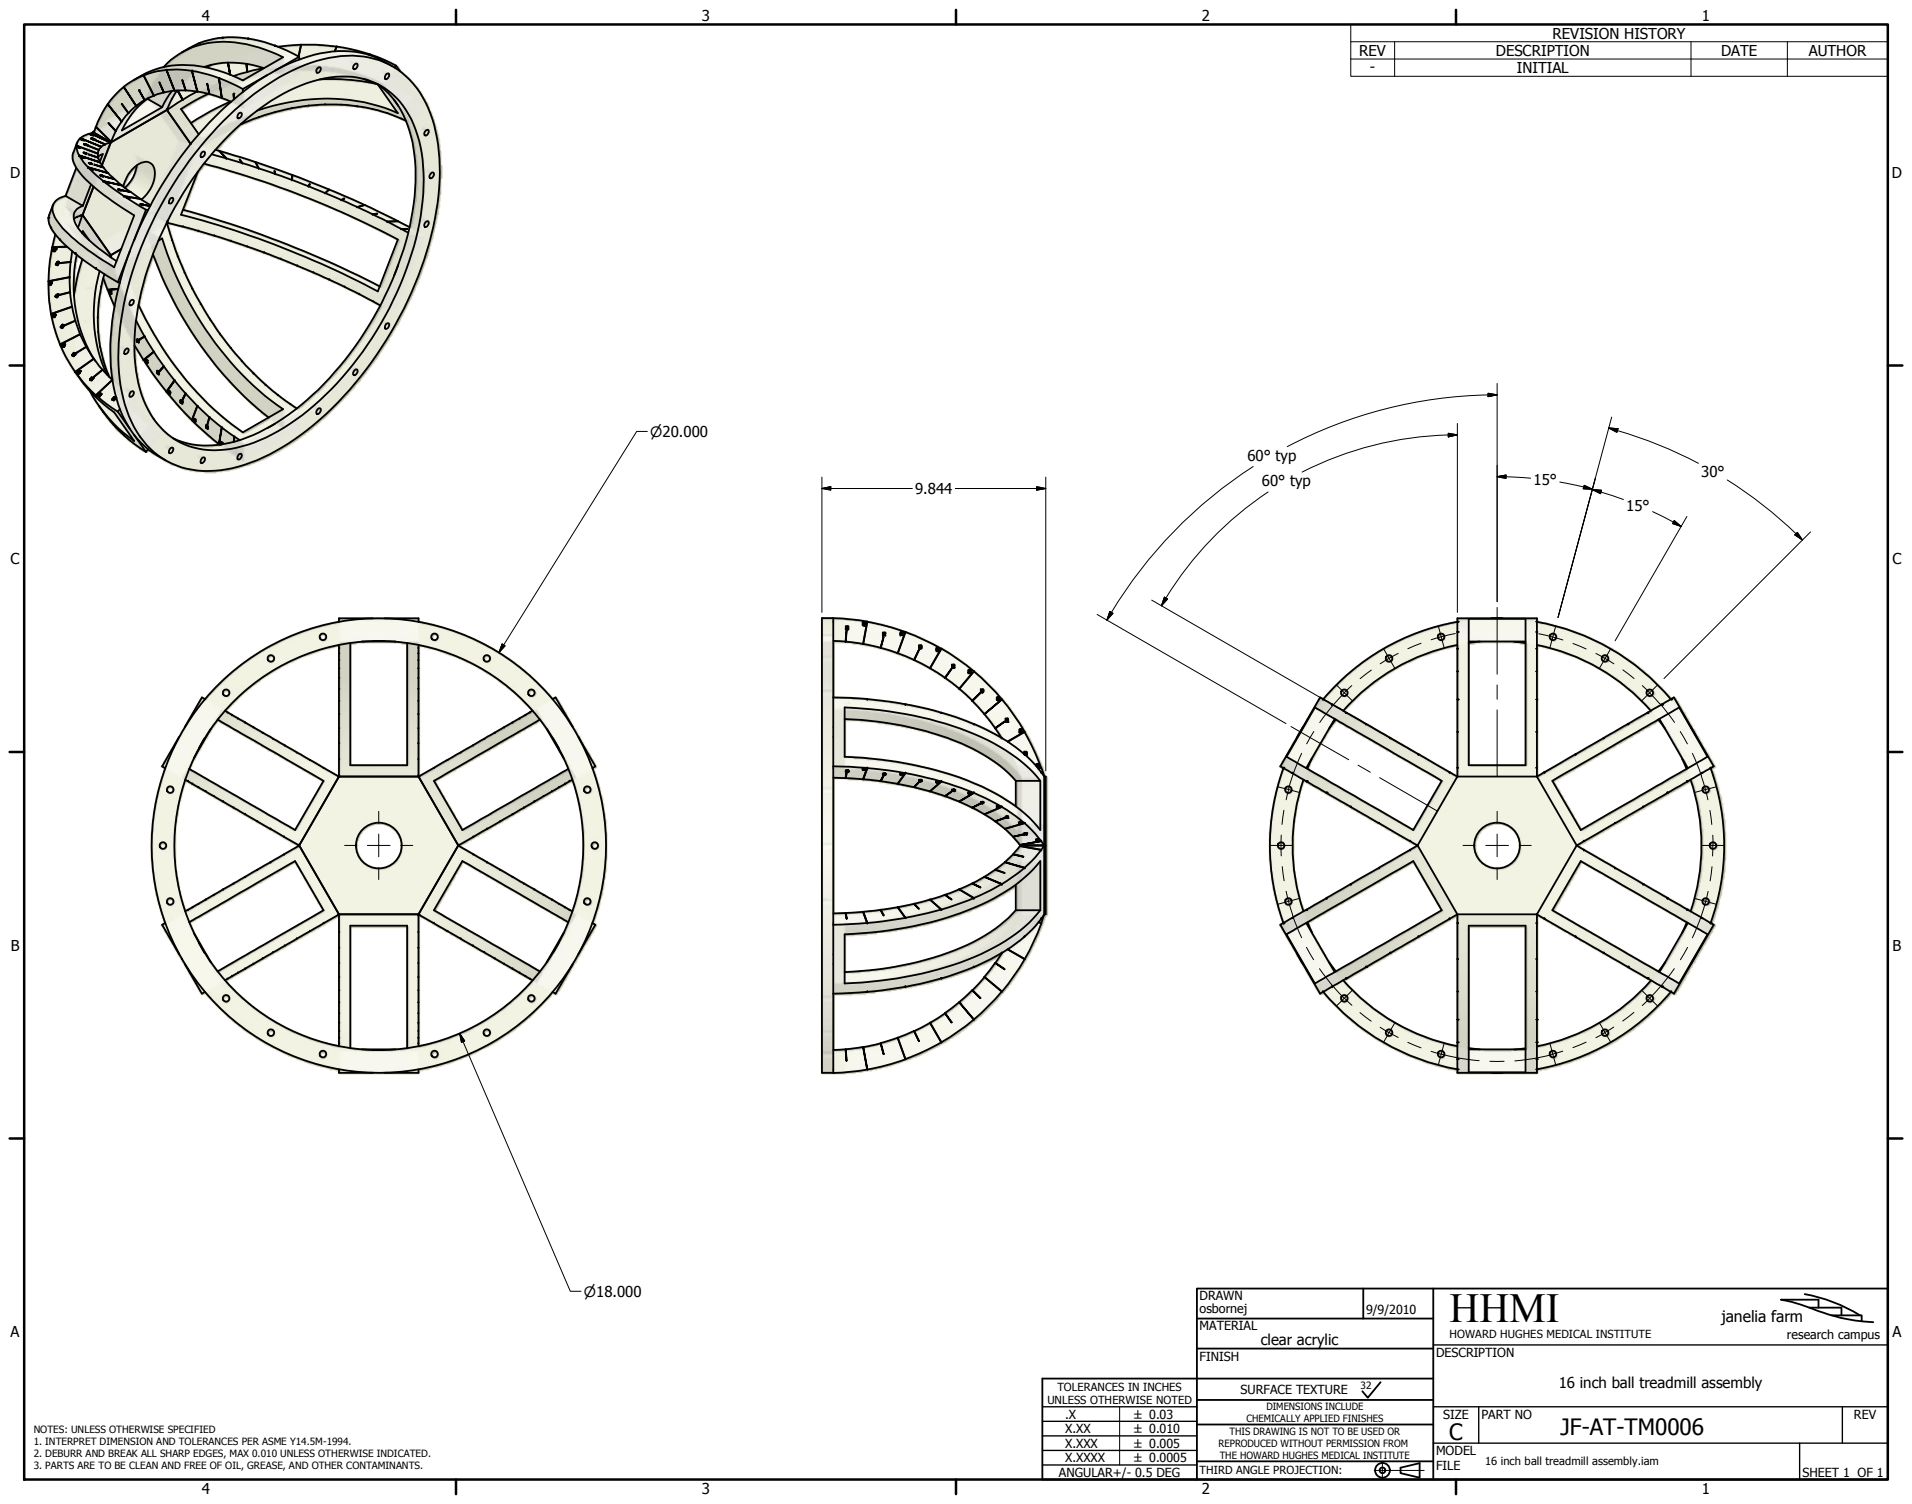
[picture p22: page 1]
SHEET 1 OF 1; DRAWN; osbornej; PART NO; SIZE C; REV; FINISH; MATERIAL; SURFACE TEXTURE; HHMI; janelia farm; research campus; MODEL FILE; X.XXXX; 16 inch ball treadmill assembly.iam; REVISION HISTORY; DESCRIPTION; DATE; AUTHOR; - INITIAL; 60° typ; clear acrylic

HOWARD HUGHES MEDICAL INSTITUTE
DESCRIPTION

16 inch ball treadmill assembly

TOLERANCES IN INCHES
UNLESS OTHERWISE NOTED
X.XXX
ANGULAR+/- 0.5 DEG

DIMENSIONS INCLUDE
CHEMICALLY APPLIED FINISHES
THIS DRAWING IS NOT TO BE USED OR
REPRODUCED WITHOUT PERMISSION FROM
THE HOWARD HUGHES MEDICAL INSTITUTE
THIRD ANGLE PROJECTION:

NOTES: UNLESS OTHERWISE SPECIFIED
1. INTERPRET DIMENSION AND TOLERANCES PER ASME Y14.5M-1994.
2. DEBURR AND BREAK ALL SHARP EDGES, MAX 0.010 UNLESS OTHERWISE INDICATED.
3. PARTS ARE TO BE CLEAN AND FREE OF OIL, GREASE, AND OTHER CONTAMINANTS.

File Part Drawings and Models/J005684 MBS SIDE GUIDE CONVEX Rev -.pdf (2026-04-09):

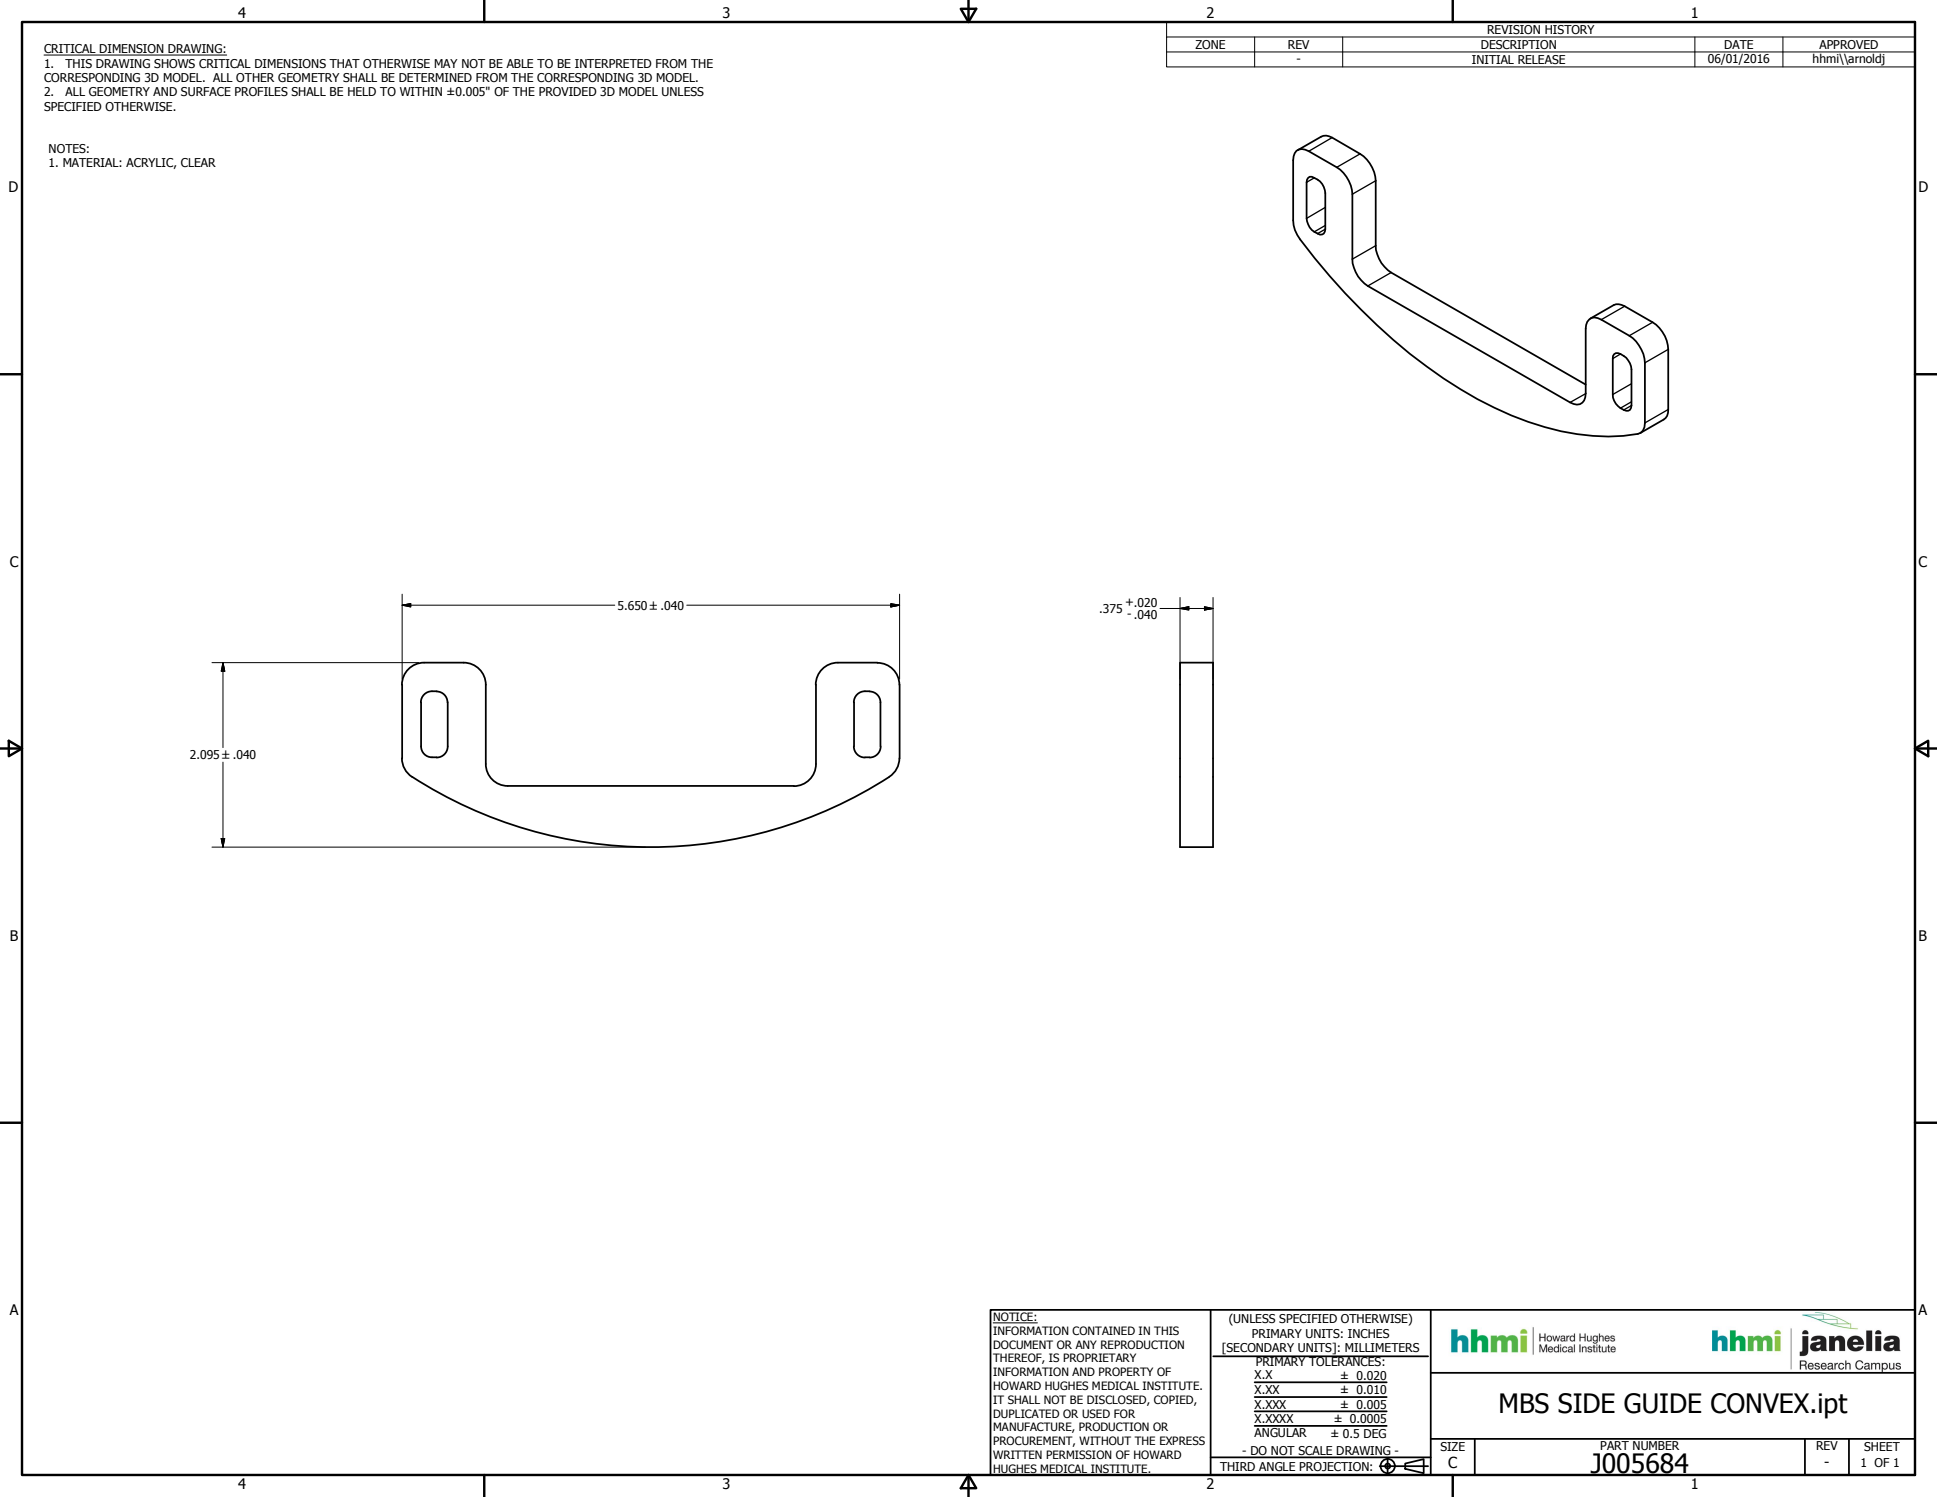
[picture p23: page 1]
PART NUMBER; SIZE; REV; SHEET; 1 OF 1 THIRD ANGLE PROJECTION:; ± 0.020 ± 0.010 ± 0.005 ± 0.0005 ± 0.5 DEG; REVISION HISTORY; ZONE; DESCRIPTION; DATE; APPROVED; INITIAL RELEASE; hhmi\\arnoldj

CRITICAL DIMENSION DRAWING:
1. THIS DRAWING SHOWS CRITICAL DIMENSIONS THAT OTHERWISE MAY NOT BE ABLE TO BE INTERPRETED FROM THE
CORRESPONDING 3D MODEL. ALL OTHER GEOMETRY SHALL BE DETERMINED FROM THE CORRESPONDING 3D MODEL.
2. ALL GEOMETRY AND SURFACE PROFILES SHALL BE HELD TO WITHIN ±0.005" OF THE PROVIDED 3D MODEL UNLESS
SPECIFIED OTHERWISE.

NOTES:
1. MATERIAL: ACRYLIC, CLEAR

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

MBS SIDE GUIDE CONVEX.ipt

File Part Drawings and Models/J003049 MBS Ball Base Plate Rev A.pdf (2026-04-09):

C

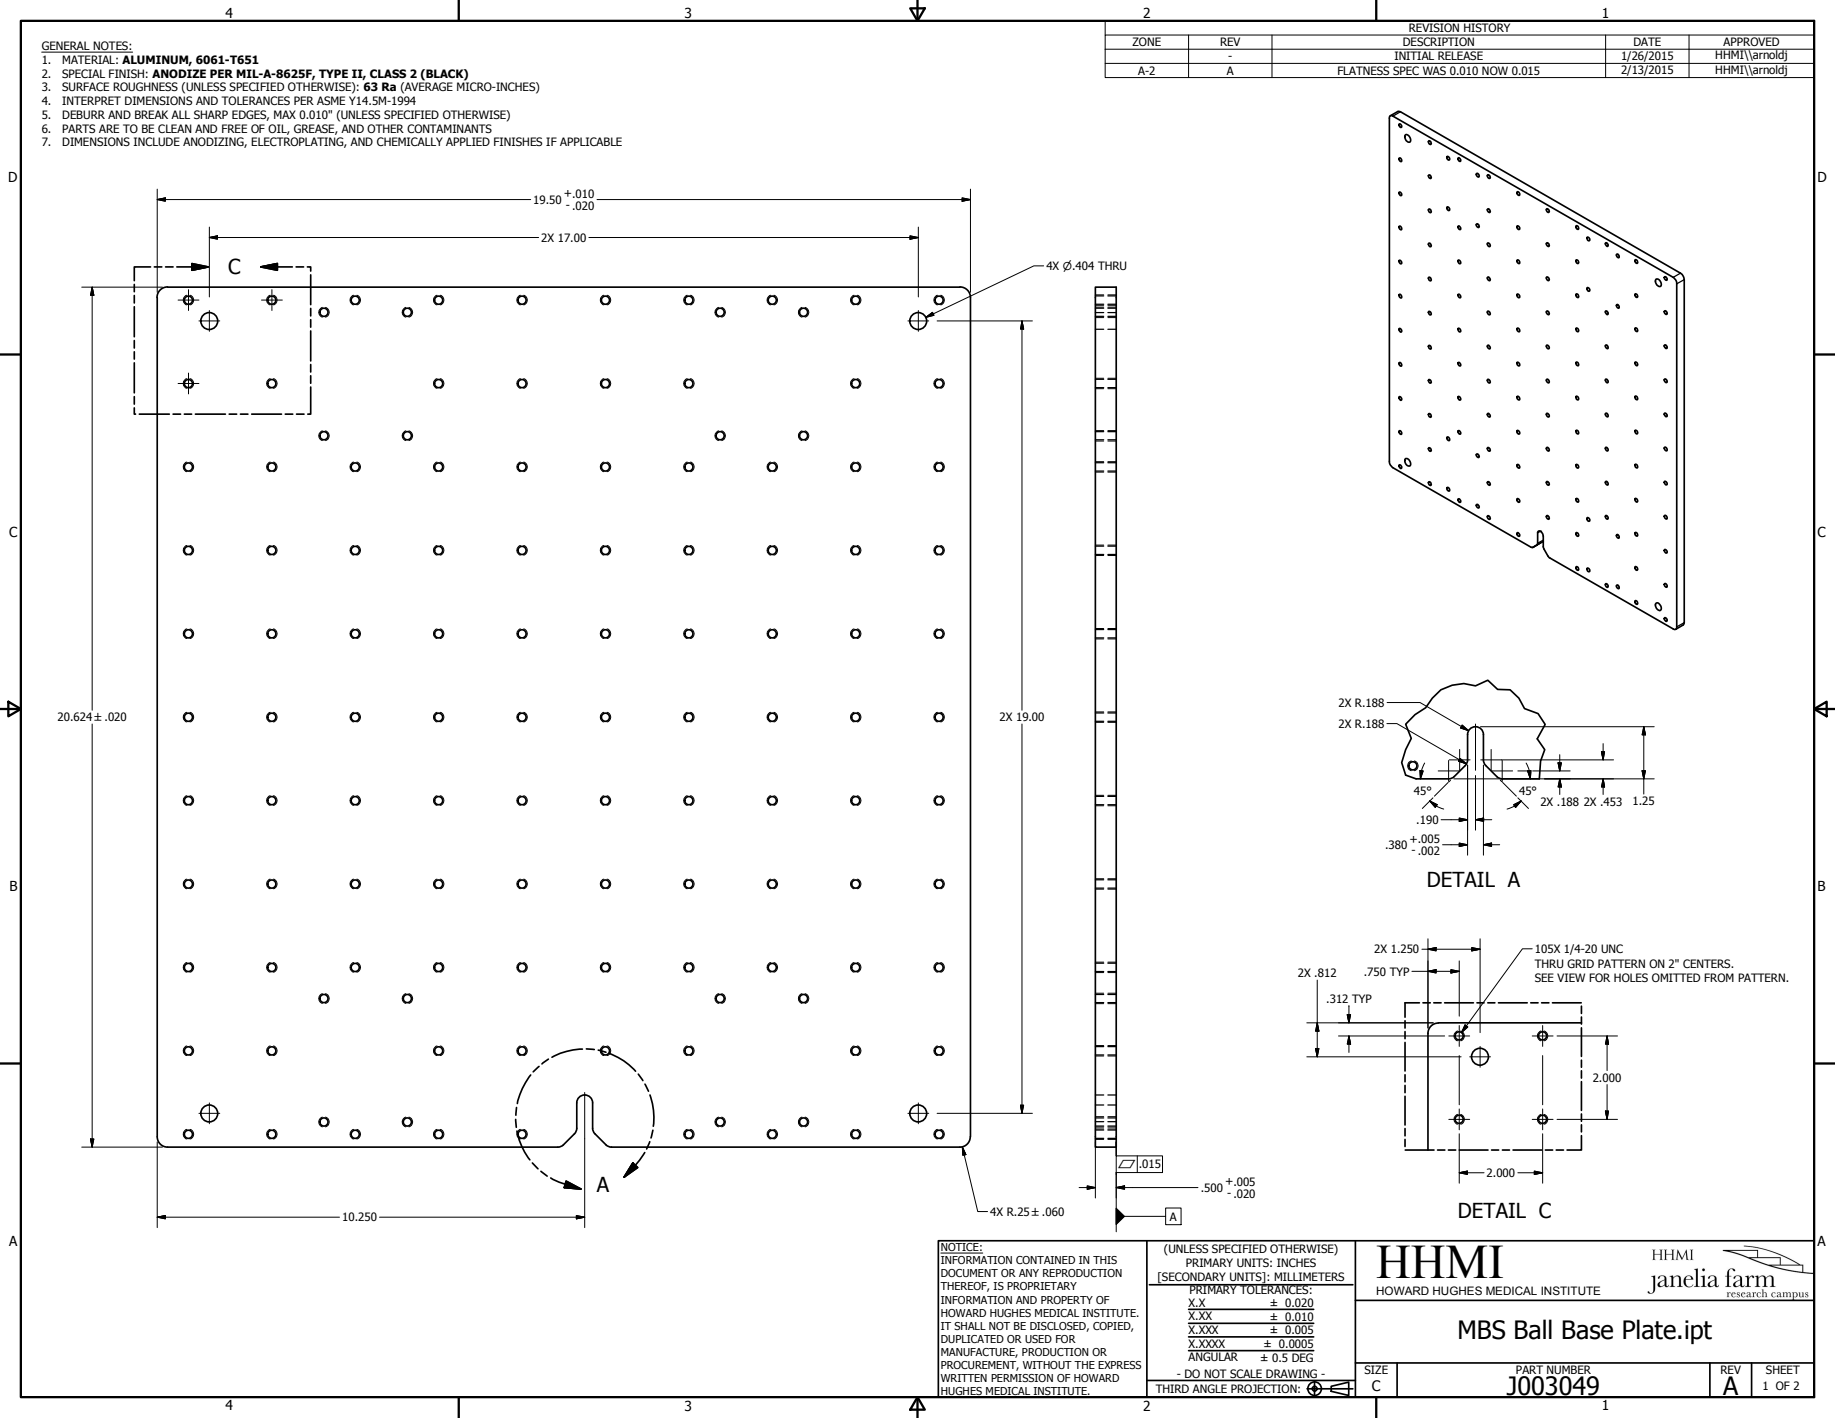
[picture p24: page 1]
DETAIL A; DETAIL C; PART NUMBER; HHMI; SIZE; REV; SHEET; 1 OF 2 THIRD ANGLE PROJECTION:; ± 0.020 ± 0.010 ± 0.005 ± 0.0005 ± 0.5 DEG; REVISION HISTORY; ZONE; DESCRIPTION; DATE; APPROVED; INITIAL RELEASE; HHMI\\arnoldj; FLATNESS SPEC WAS 0.010 NOW 0.015; .750 TYP; .312 TYP; 4X P.404 THRU

GENERAL NOTES:
1. MATERIAL: ALUMINUM, 6061-T651
2. SPECIAL FINISH: ANODIZE PER MIL-A-8625F, TYPE II, CLASS 2 (BLACK)
3. SURFACE ROUGHNESS (UNLESS SPECIFIED OTHERWISE): 63 Ra (AVERAGE MICRO-INCHES)
4. INTERPRET DIMENSIONS AND TOLERANCES PER ASME Y14.5M-1994
5. DEBURR AND BREAK ALL SHARP EDGES, MAX 0.010" (UNLESS SPECIFIED OTHERWISE)
6. PARTS ARE TO BE CLEAN AND FREE OF OIL, GREASE, AND OTHER CONTAMINANTS
7. DIMENSIONS INCLUDE ANODIZING, ELECTROPLATING, AND CHEMICALLY APPLIED FINISHES IF APPLICABLE

105X 1/4-20 UNC
THRU GRID PATTERN ON 2" CENTERS.
SEE VIEW FOR HOLES OMITTED FROM PATTERN.

NOTICE:
INFORMATION CONTAINED IN THIS
DOCUMENT OR ANY REPRODUCTION
THEREOF, IS PROPRIETARY
INFORMATION AND PROPERTY OF
HOWARD HUGHES MEDICAL INSTITUTE.
IT SHALL NOT BE DISCLOSED, COPIED,
DUPLICATED OR USED FOR
MANUFACTURE, PRODUCTION OR
PROCUREMENT, WITHOUT THE EXPRESS
WRITTEN PERMISSION OF HOWARD
HUGHES MEDICAL INSTITUTE.

(UNLESS SPECIFIED OTHERWISE)
PRIMARY UNITS: INCHES
[SECONDARY UNITS]: MILLIMETERS
PRIMARY TOLERANCES:
X.XXX
X.XXXX
ANGULAR
- DO NOT SCALE DRAWING -

HOWARD HUGHES MEDICAL INSTITUTE

MBS Ball Base Plate.ipt

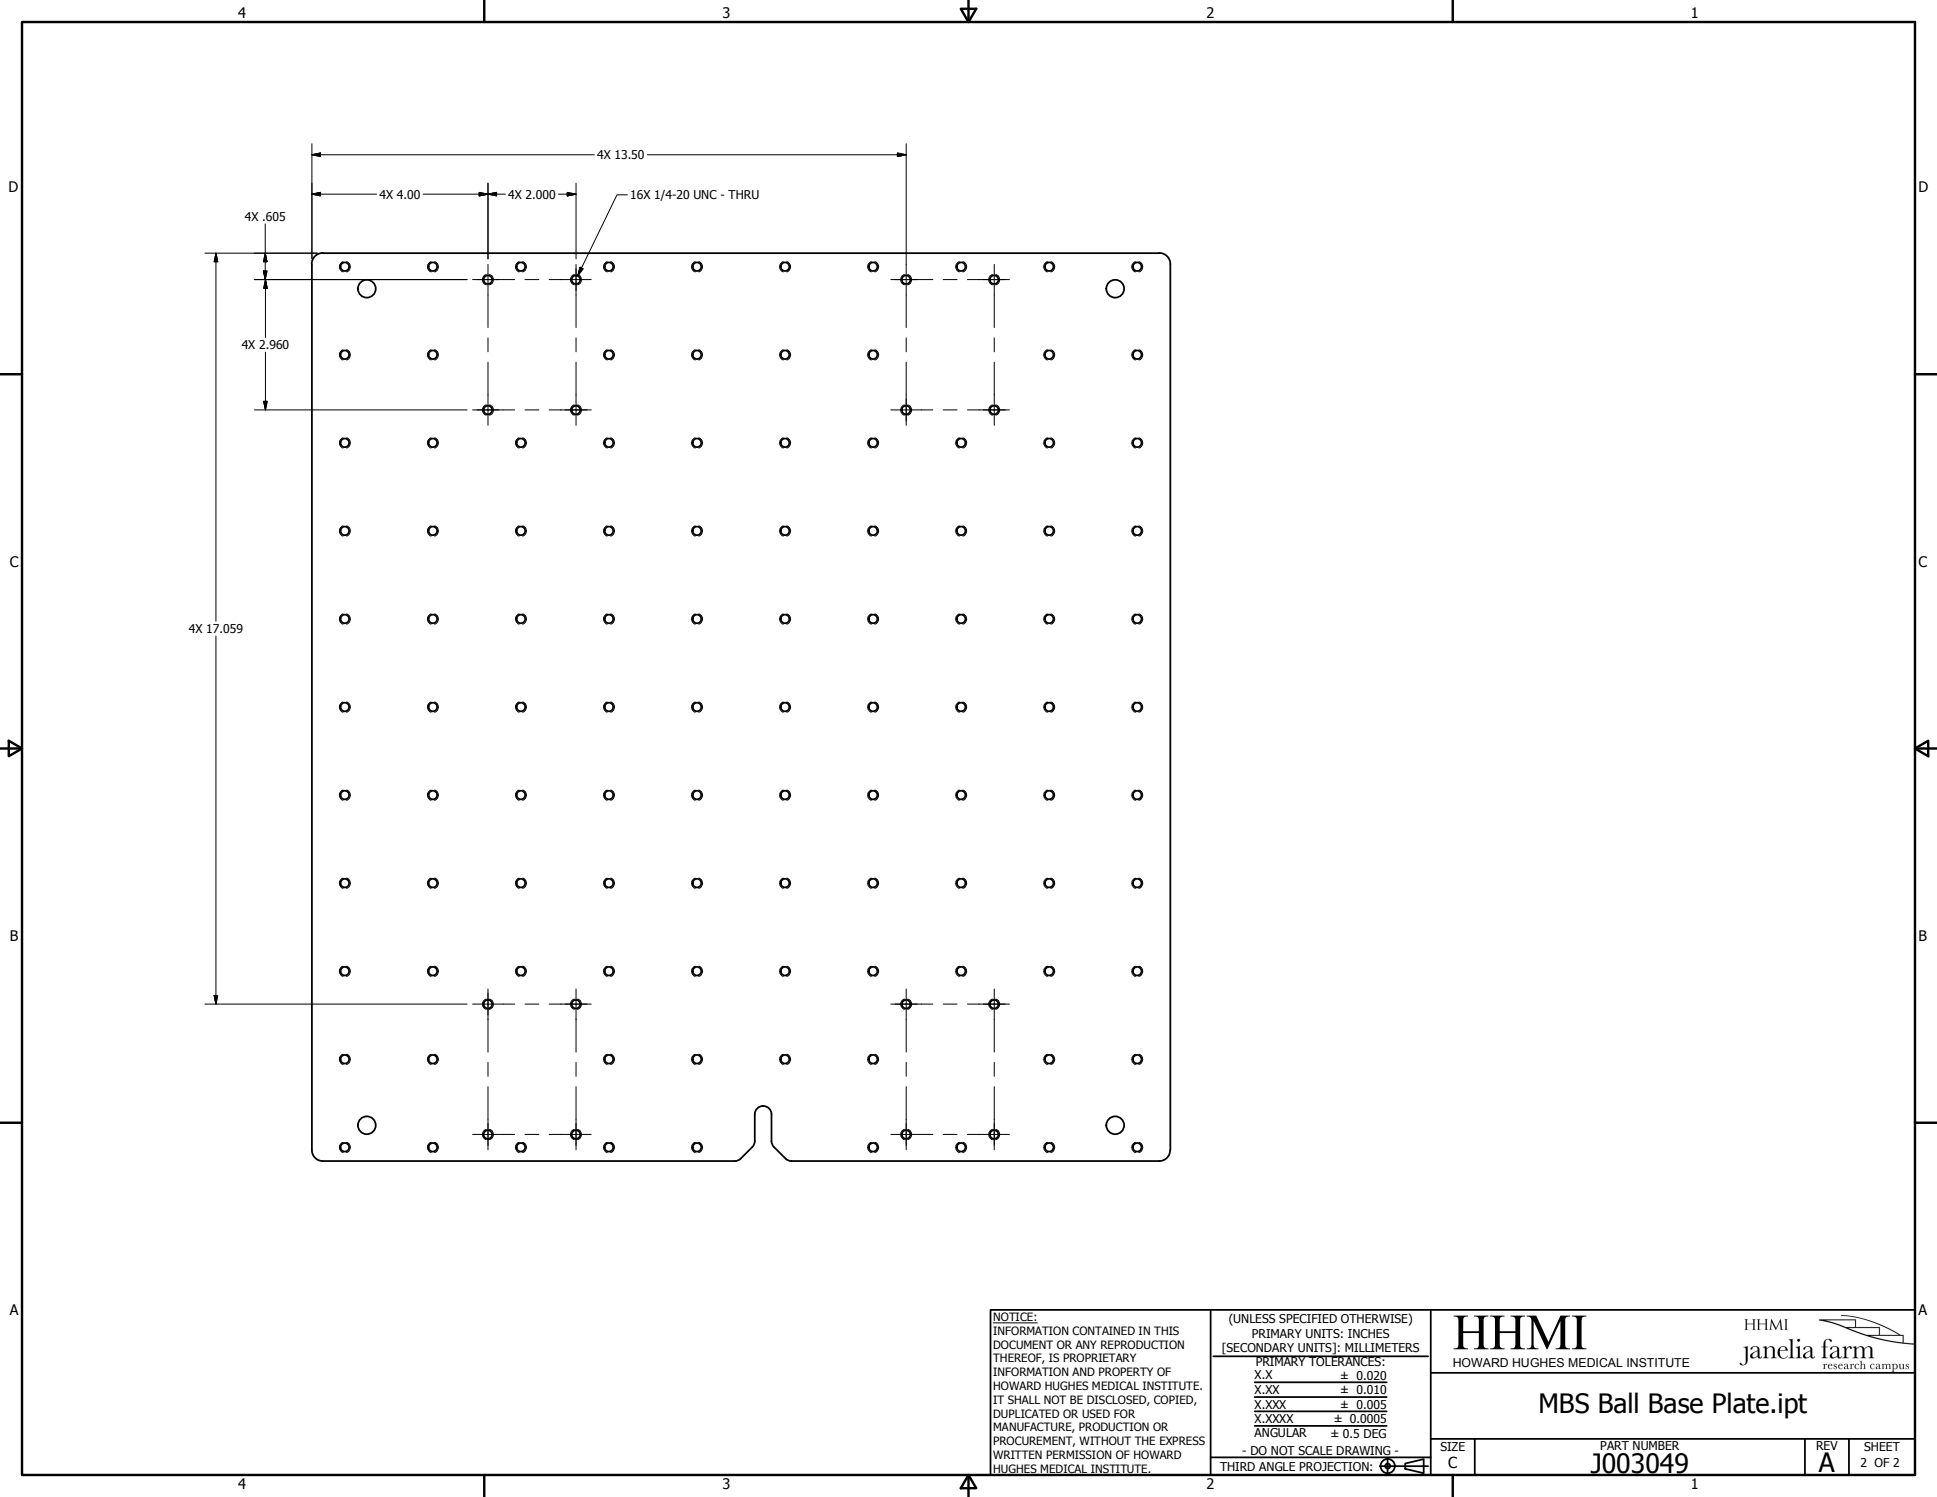
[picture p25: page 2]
PART NUMBER; HHMI; SIZE; REV; SHEET; 2 OF 2 THIRD ANGLE PROJECTION:; ± 0.020 ± 0.010 ± 0.005 ± 0.0005 ± 0.5 DEG; 16X 1/4-20 UNC - THRU

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

HOWARD HUGHES MEDICAL INSTITUTE

MBS Ball Base Plate.ipt
